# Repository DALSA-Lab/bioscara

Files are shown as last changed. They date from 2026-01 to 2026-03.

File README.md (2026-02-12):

# icon Bioscara - DALSA DIY SCARA robot arm
This repository serves to collect all information regarding DALSA's DIY robot arm **Bioscara**.
<p align="center">
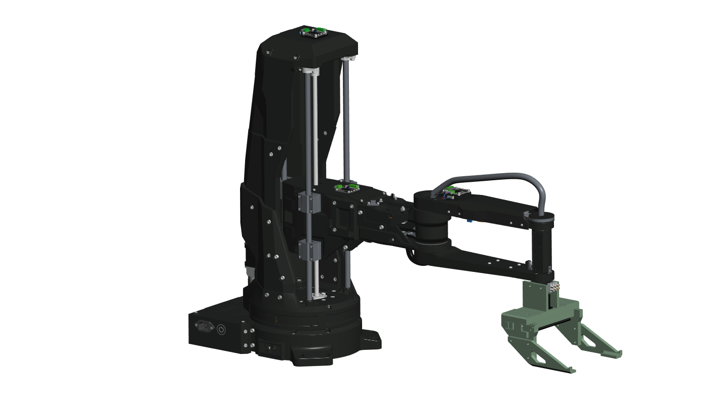
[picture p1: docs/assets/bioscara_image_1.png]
  
</p>

## Documentation and Guides
Please refer to the user guides and source code documentation at: https://dalsa-lab.github.io/bioscara/

> [!NOTE]  
> If the website is unavailable, you can find its source code in the *docs/* directory

## Repository Structure
The repository structure is based on the DALSA template.

- ***docs/***: Contains the user-guides as *.md* files and serves as the source code for the Sphinx documentation
- ***hardware/***: Contains the robots CAD model as a STEP file, STL meshes, electrical schematics and further documents
- ***installation/***: Contains installation scripts and files.
- ***lib/***: Contains the source code for the ROS2 workspace and joint firmware.
- ***test/***: Contains system test data and test protocols.

## Branches
There are three core branches which MUST NOT be deleted without appropriate replacement.
- ***main***: This branch contains the latest stable source code. Any commit to this branch will automatically trigger the build of a new documentation.
- ***bioscara_v1***: Contains the original Bioscara project by Karol Garbor.
- ***gh-pages***: contains the HTML source code hosted at https://dalsa-lab.github.io/bioscara/

## Dependencies
Currently the project has the following source-code dependencies:
- [***single_trigger_controller***](https://github.com/DALSA-Lab/ros2_control-single_trigger_controller.git) branch: *main*
- [***moveit_task_constructor***](https://github.com/moveit/moveit_task_constructor.git) branch: *ros2*
- [***moveit2***](https://github.com/DALSA-Lab/moveit2-dalsa.git) branch: *main*
- [***moveit_visual_tools***](https://github.com/moveit/moveit_visual_tools.git) branch: *ros2*
- [***pick_ik***](https://github.com/PickNikRobotics/pick_ik.git) branch: *main*

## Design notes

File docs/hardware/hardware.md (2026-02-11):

# Supplementary Assembly Instructions
The hardware has been modified in comparison the original Bioscara project.

bioscara

## Key Modifications
The key changes were:
- Replacing the MKServo42C closed-loop stepper drivers with UStepper S32 drivers
- Removing the optical endstops and replacing them with physical stop blocks for sensor less homing
- Removing the associtated wiring to the optical endstops and MKServo drivers.
- The UStepper drivers only require two signal wires (SDA/SCL) and the 24V/GND power cables.
- The electronics compartment has been simplified since the 3D-printer motherboard could be removed.
- All wires have been replaced and properly sized and terminated.
- Power distribution is achieved through terminal block mounted on DIN-rails.
- The gripper has been redesgined.

### Joint driver
The new joint driver is mounted on the back of the stepper motors just like the MKServo 42C drivers. 

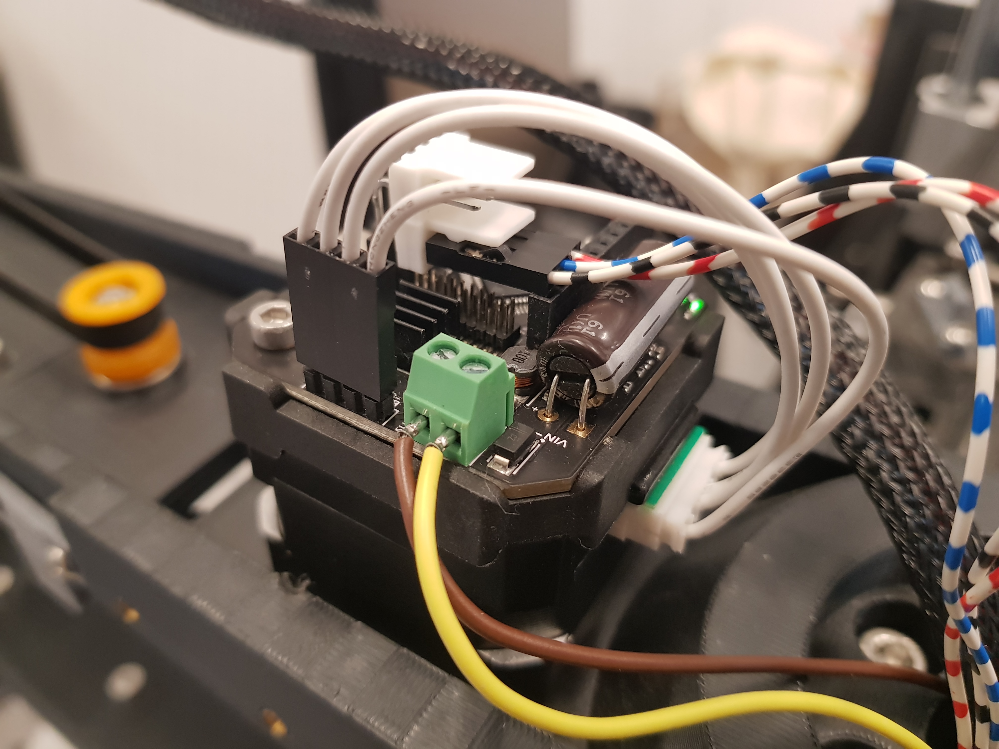
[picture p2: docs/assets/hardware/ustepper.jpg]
UStepper S32


**TO-DO:**
- Increase the cutout dimensions in the J2 covers and J1 Top cover to make room for the slightly larger UStepper mounts.

### Endstops
See the new endstops in the figures below. Their STL file can be found in the *hardware/meshes/* directory.

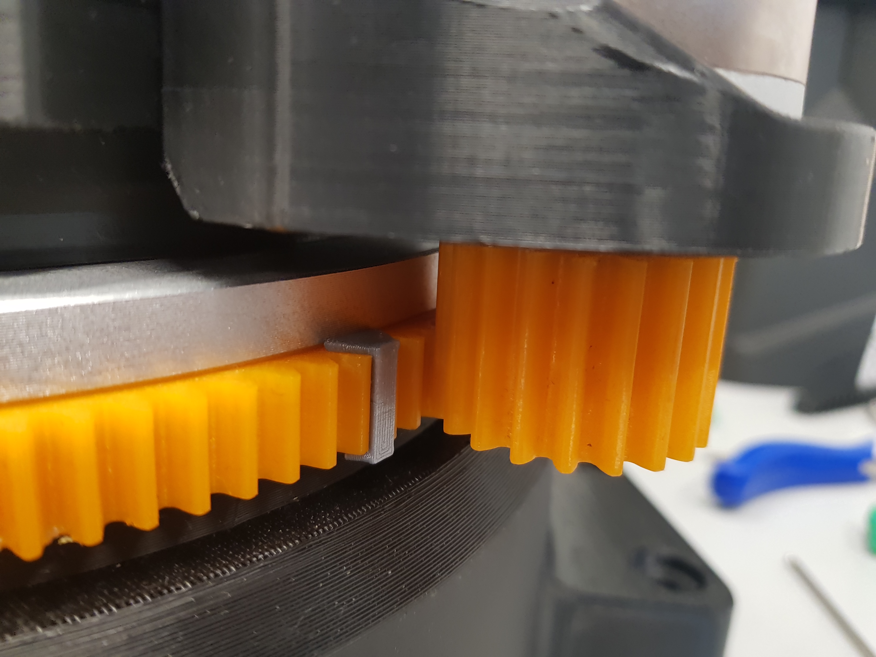
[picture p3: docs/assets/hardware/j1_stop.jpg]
J1 Endstop
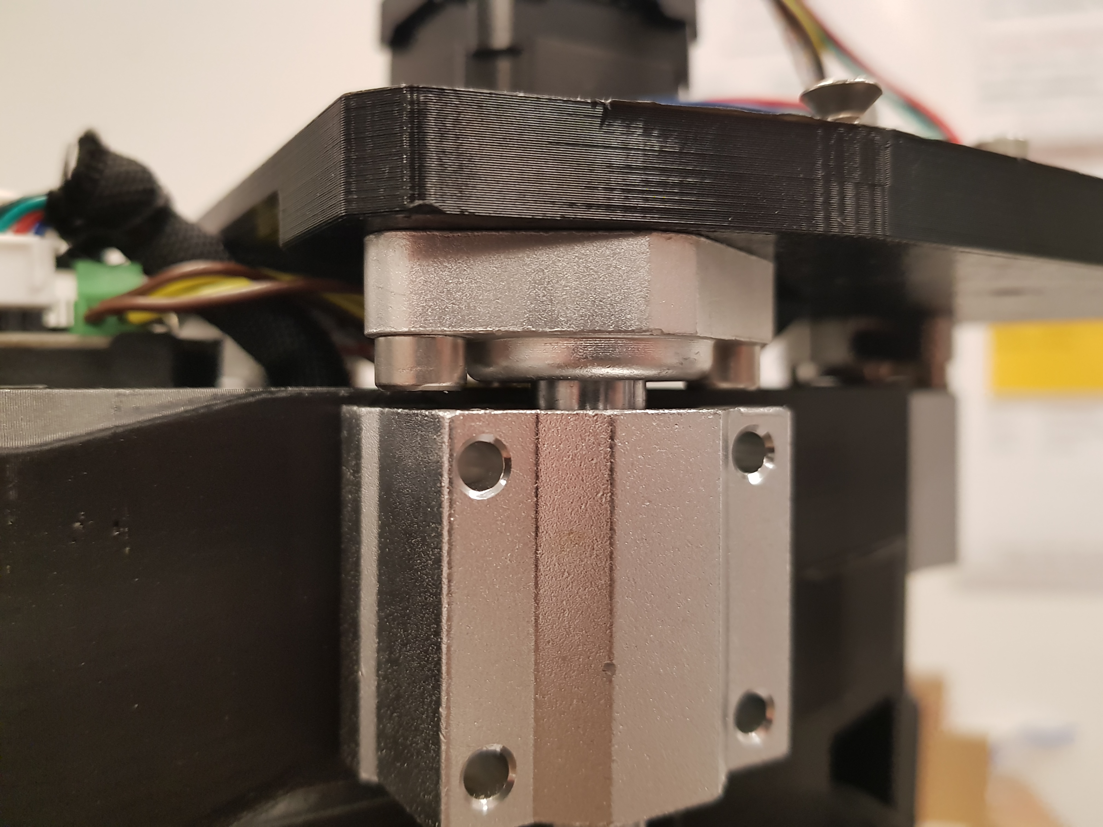
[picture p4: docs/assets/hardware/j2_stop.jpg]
J2 Endstop
|  |  |
|---|---|
| **J1 Endstop** | **J2 Endstop** |

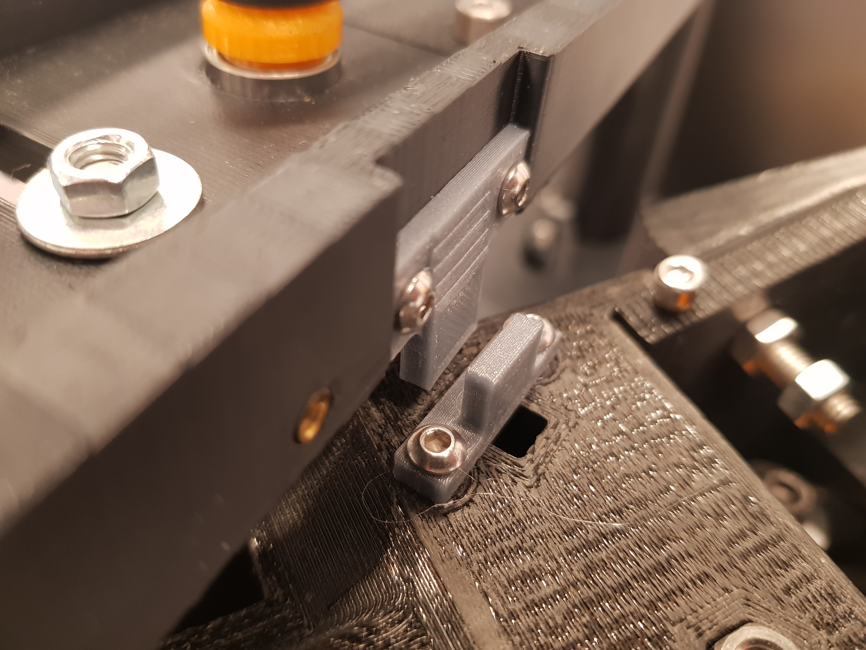
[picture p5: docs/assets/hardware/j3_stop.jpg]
J3 Endstop
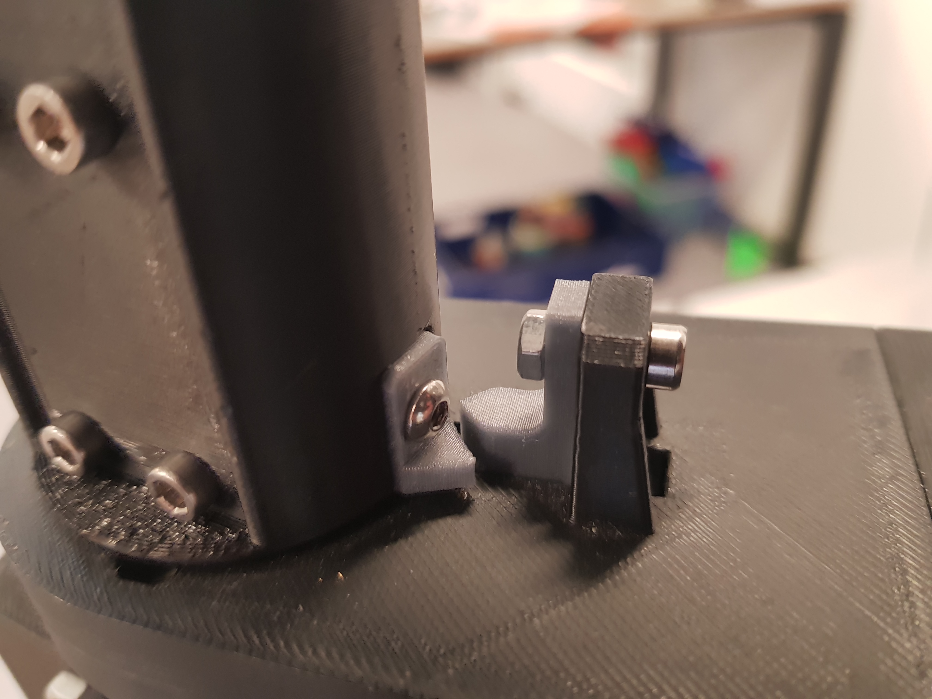
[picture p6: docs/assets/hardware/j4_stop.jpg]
J4 Endstop
|  |  |
|---|---|
| **J3 Endstop** | **J4 Endstop** |

### New Gripper Assembly
The new gripper was designed in June 2025. The results are presented in a [presentation](../../hardware/gripper_redesign_project_presentation.pdf) and [report](../../hardware/gripper_redesign_project_report.pdf).

The CAD files can be found under the *hardware/CAD Model/gripper_v2* directory.

### Tensioner Pulley Slipping
The J4 belt drive needs to be redesigned, since the tensioner pulley slips under load, releasing tension. The current workaround is the *tensioner_stop_block* that is inserted in the slot to prevent the pulley from sliding back. The stop block needs to be printed and inserted as shown in the figure. 

**TO-DO:**
- Fix the design, for example by "knurling" the surface to increase its roughness to increase friction.

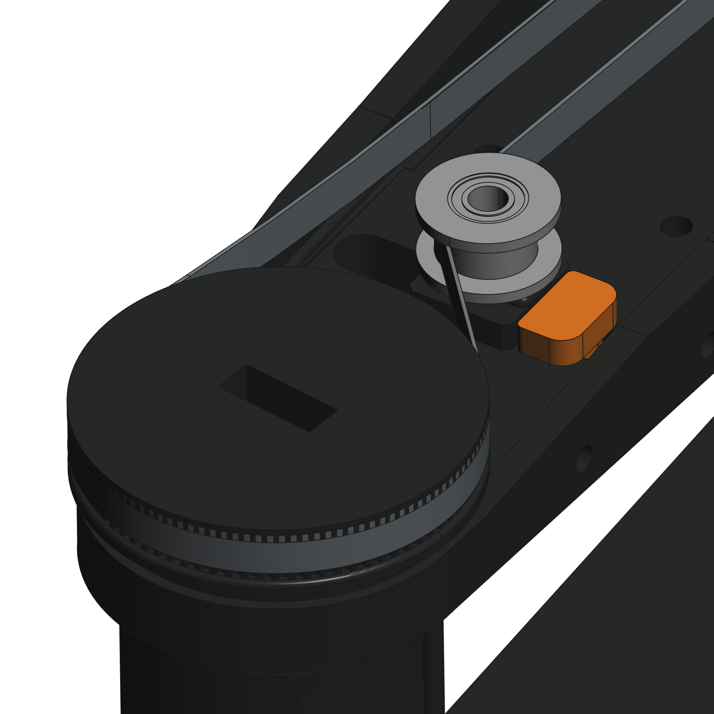
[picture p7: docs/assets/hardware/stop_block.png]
Stop Block


### Electrical Design
The electrical schematic can be found [here](../../hardware/schematics/schematic.pdf).

The schematic shows how to wire the new joint controllers and how to distribute the power in the terminal blocks.
For indicative cable lengths and wire gauges refer to the schematic as well.

:::{important}
All wires shall be appropriatly sized and terminated with spade connectors for the power supply and ferrules for screw terminals.
:::

:::{note}
Some images may display a seperate GND connection with the I2C wires. This is no longer correct. The wiring as displayed in the schematic with only a single GND wired to the power terminals is correct.
:::

The AC wiring was redone. Note that the wires are properly terminated. The power switch was replaced with a simple switch.

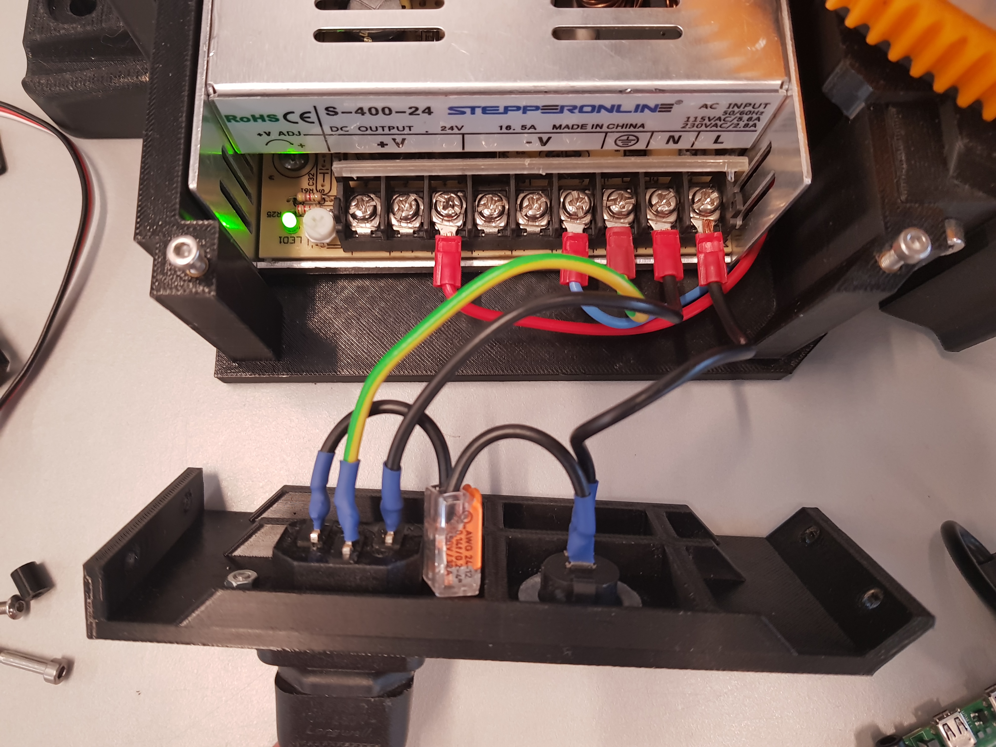
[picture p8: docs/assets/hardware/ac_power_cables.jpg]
AC cables


### Simplified Electronics Compartment
The 3D-printer motherboard and level-shifter was removed from the base plate. The number of wires was reduced. The new design is shown in the figure below. 
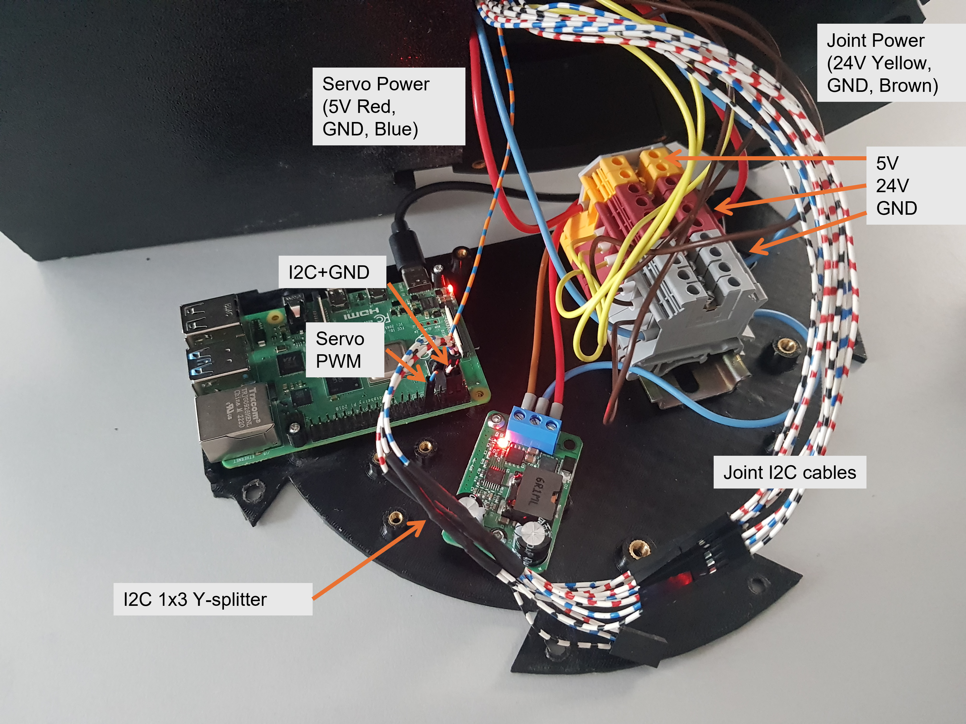
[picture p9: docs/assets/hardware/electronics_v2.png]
Electronics baseplate


**TO-DO:**
- Redesigning the electronics base plate to be able to properly mount all components. The terminal block are currently just glued in place.

## Assembly Instructions
The assmbley instructions are given in [this pdf](../../hardware/Bioscara_v2_manual_preliminary.pdf).

:::{tip}
A video of the original assembly can be found in [this  YouTube video](https://www.youtube.com/watch?v=obPP-tCtBTw).
:::

**TO-DO:**
- The instructions have only been preliminarily updated. A unified assembly guide with up to date images and information needs to be compiled.
- The current assembly guide is PowerPoint presentation. This file format is very poor for version control. The new assembly guide needs to full-fill the following criteria:
    - Platform independent: The new guide shall be easily maintainable from different platforms. PowerPoint is poorly portable between operating systems.
    - Version Control: The new guide shall be written in a text based format that supports version control such as this document or Latex.

## CAD Model and STL Meshes
The complete STEP CAD model can be found in the *hardware/CAD_model/* directory. The STEP file is compressed as a ZIP archive to be able to upload it to Github. The STL meshes for 3D-printing are in the *hardware/meshes/*.

:::{tip}
The original, now outdated, Bioscara_v1 STEP files can be found [here](https://a360.co/3SWc07A)
:::

**TO-DO:**
- The coordinate systems of the CAD model are completely wrong and need to be fixed
- The CAD model does not include the simplified arm shape used in the robot description URDF files, this remains to be added.

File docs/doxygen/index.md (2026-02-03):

# Bioscara C++ API Documentation
This is the API documentation for the Bioscara robotic control middleware based on the ROS2 framework.

Please find the key components below:
- bioscara_joint_firmware: contains the joint firmware and its associtated helper classes.
- bioscara_hardware_drivers: contains the BaseJoint, Joint and MockJoint drivers as well as the BaseGripper, Gripper and MockGripper drivers.
- bioscara_hardware_interfaces: contains the ros2_control hardware interfaces that implement the Bioscara arm and gripper hardware components in the BioscaraArmHardwareInterface and BioscaraGripperHardwareInterface respectively.
- bioscara_rviz_plugin: contains the BioscaraPanel Rviz GUI panel.
- single_trigger_controller::SingleTriggerController: contains the documentation for the SingleTriggerController.

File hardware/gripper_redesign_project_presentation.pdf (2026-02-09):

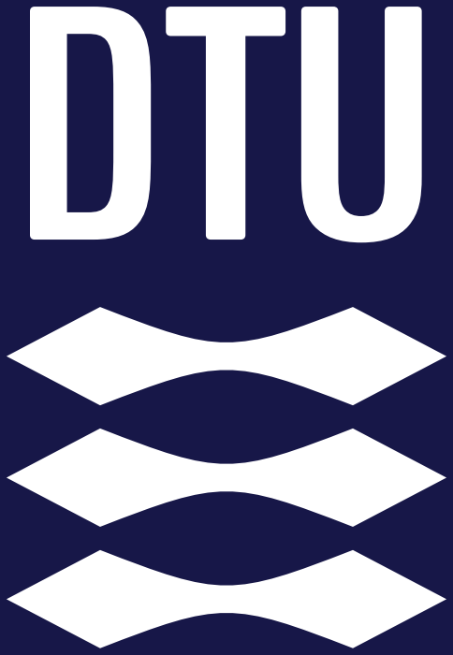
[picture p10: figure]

# Upgrading a 3D-Printed Gripper for Enhanced Robotic Handling

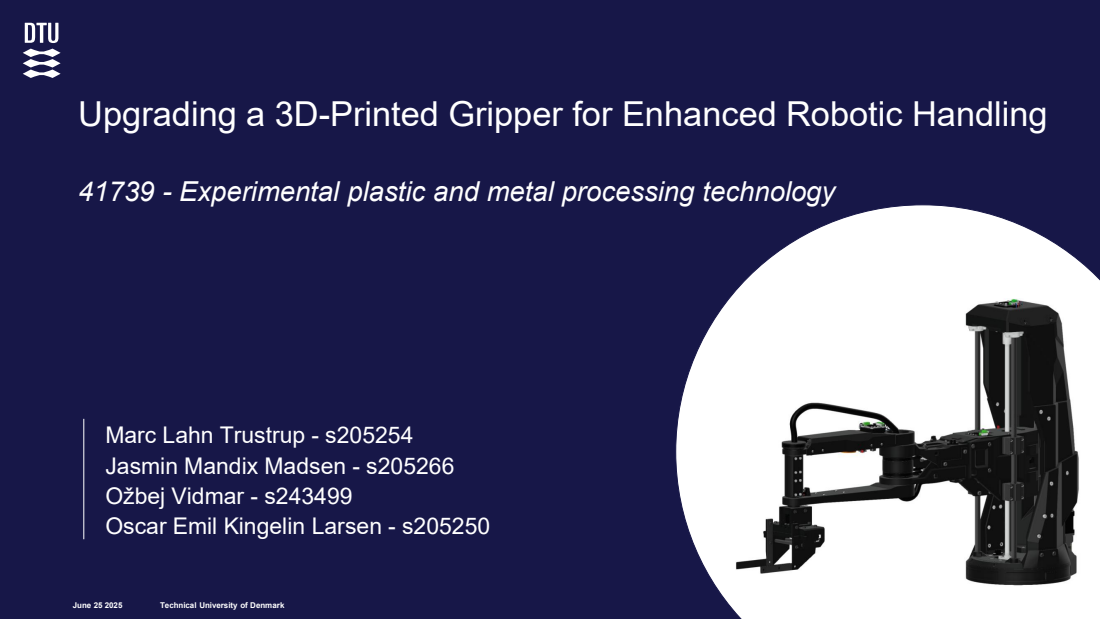
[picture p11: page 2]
June 25 2025

41739 - Experimental plastic and metal processing technology

Marc Lahn Trustrup - s205254
Jasmin Mandix Madsen - s205266
Ožbej Vidmar - s243499
Oscar Emil Kingelin Larsen - s205250

Technical University of Denmark

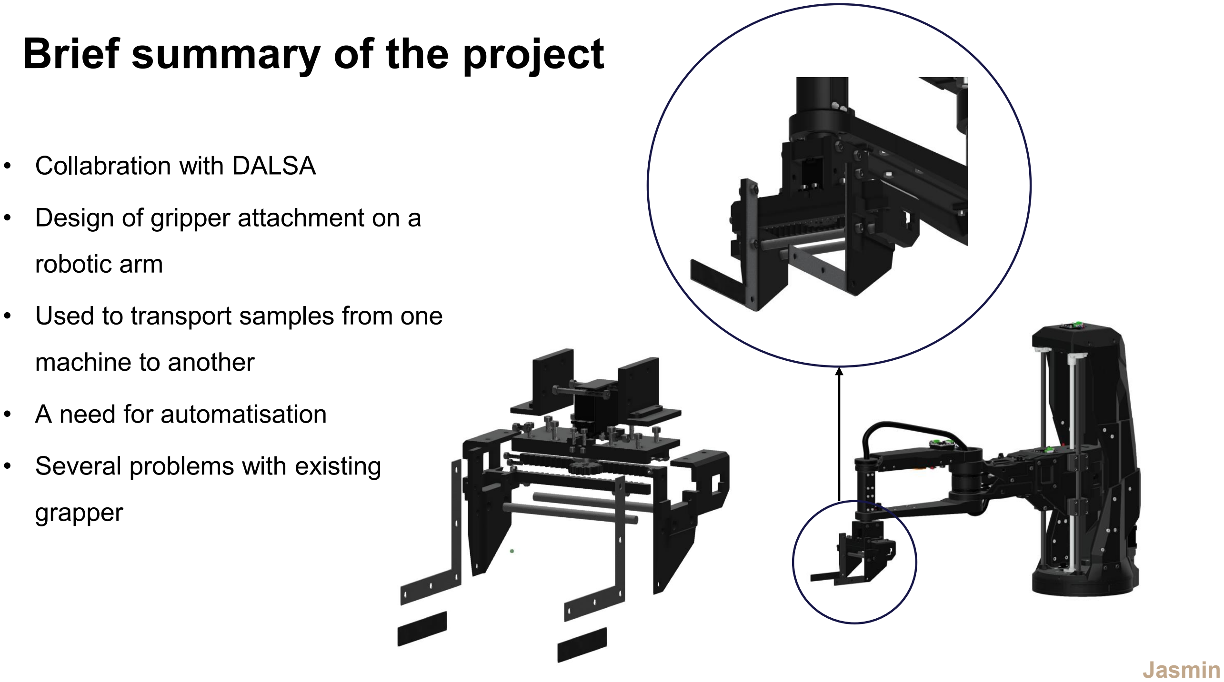
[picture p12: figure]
Brief summary of the project; • Collabration with DALSA; • Design of gripper attachment on a; robotic arm; • Used to transport samples from one; machine to another; • A need for automatisation; • Several problems with existing; grapper; Jasmin

3

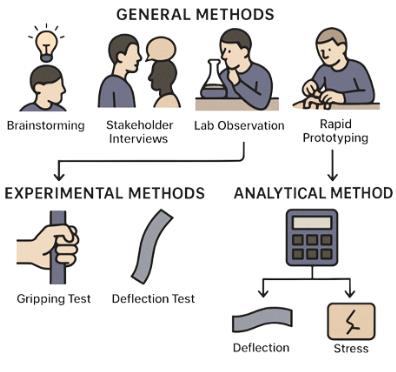
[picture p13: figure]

Technical University of Denmark | 4

# Methodology of the project

General methods
- Brainstorming
- Stakeholder interviews
- Lab observations
- Rapid prototyping

Experimental methods
- Gripping test
- Deflection test

Analytical method
- Force analysis
- Deflection
- Stress

Jasmin

# Final iteration Base

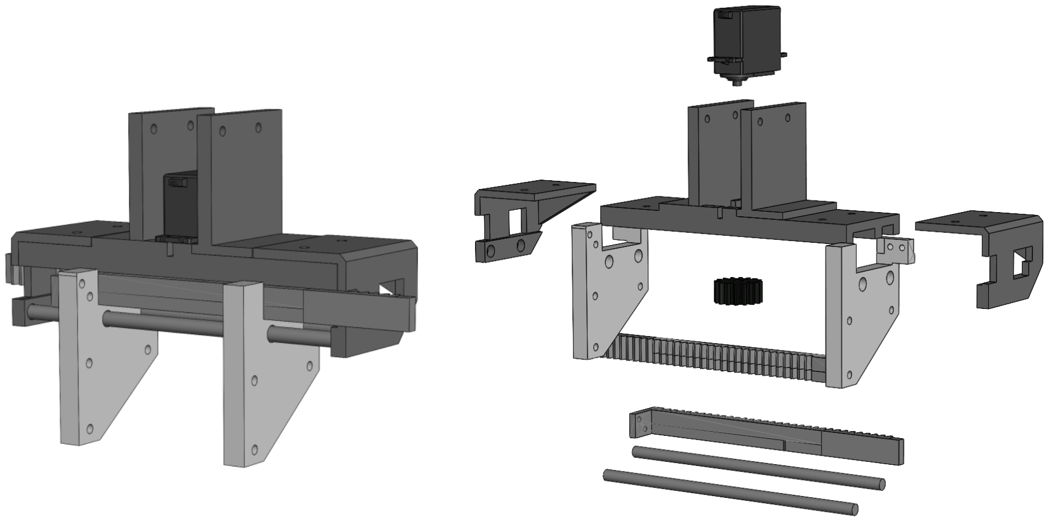
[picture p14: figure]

5

- Extended design
- Increased thickness
- Supports added
- Metal rods (new since last week)

Jasmin

# Final iteration gripper

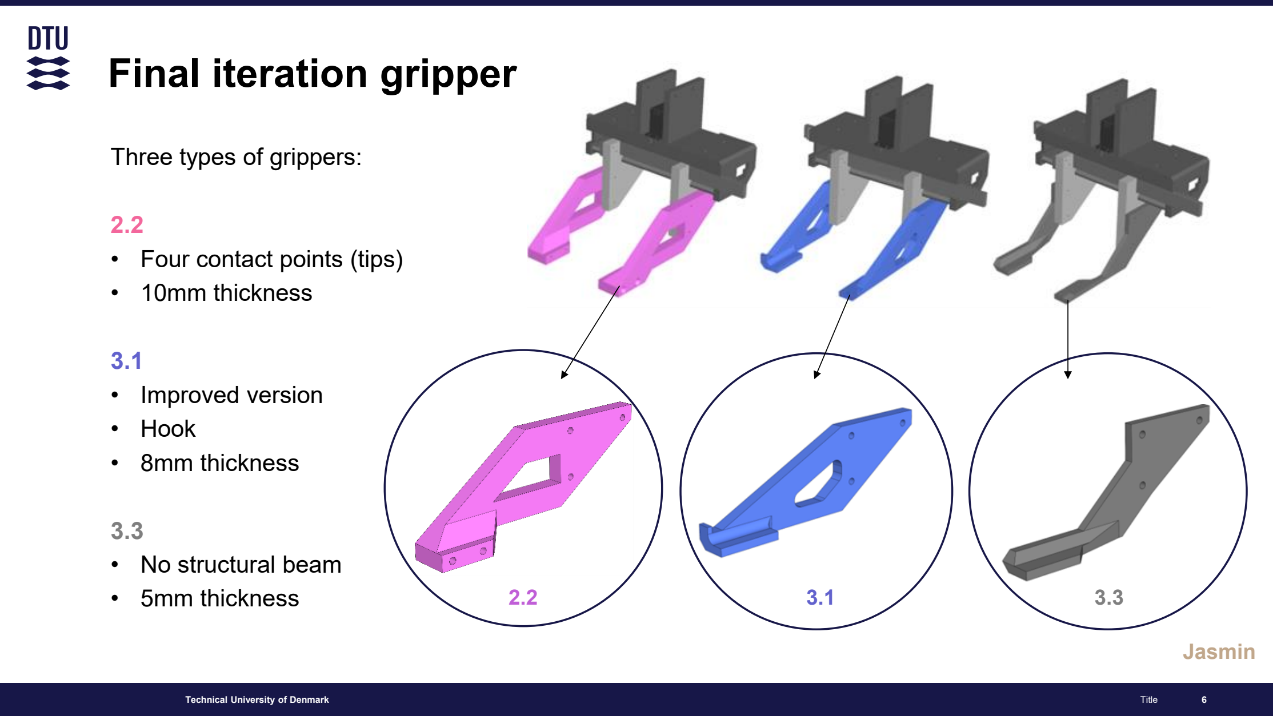
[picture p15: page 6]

Title | 6

Three types of grippers:

2.2
- Four contact points (tips)
- 10mm thickness

3.1
- Improved version
- Hook
- 8mm thickness

3.3
- No structural beam
- 5mm thickness | 2.2 | 3.1 | 3.3

Jasmin

# 1. Experiment: Gripping test

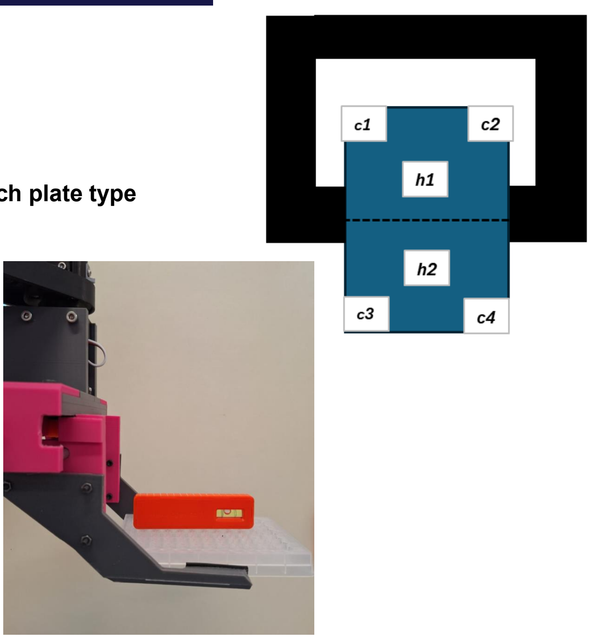
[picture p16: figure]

7

Test sequence was performed for each gripper and each plate type

1. Grip the empty plate
2. Apply the maximum load in the center
3. Apply half the maximum weight at either end
4. Apply a quarter of the total weight in each corner

Ožbej

# Results from the gripping test

8

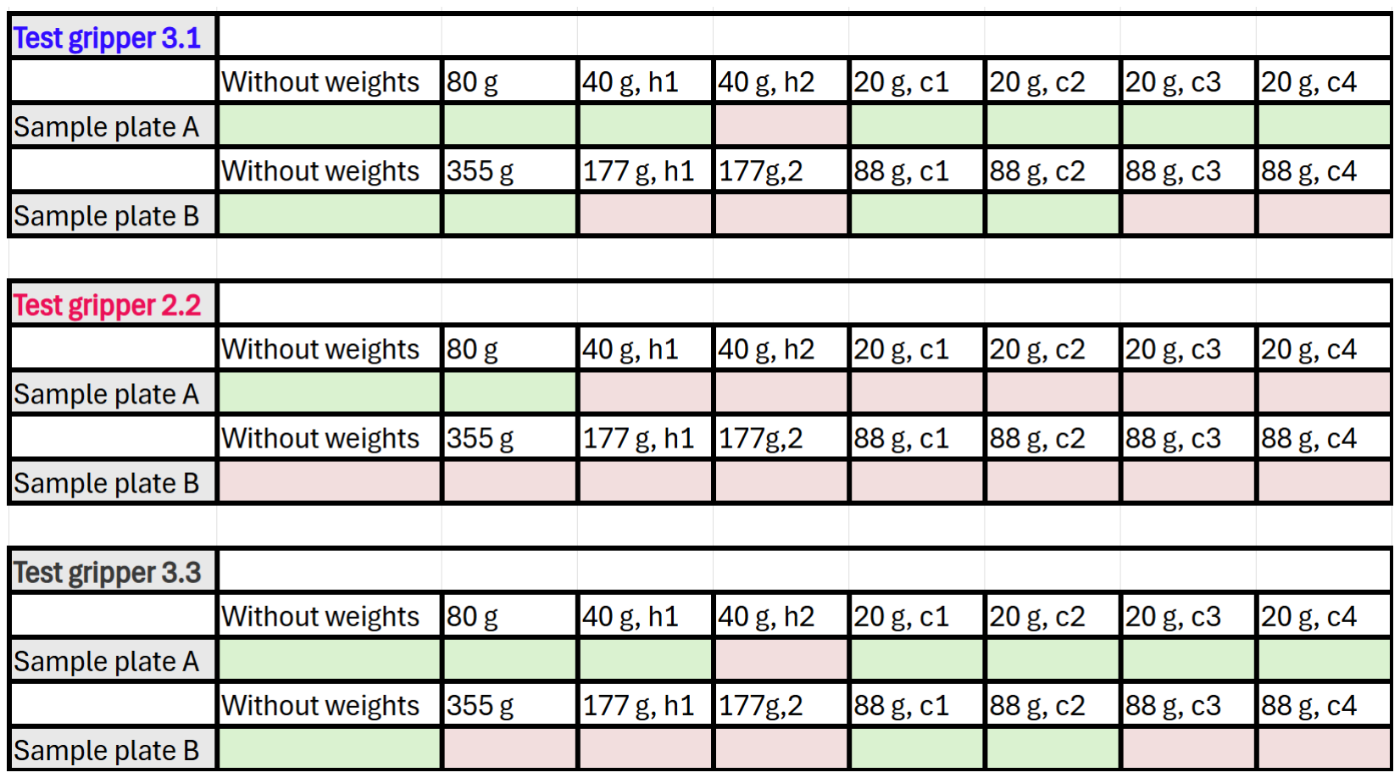
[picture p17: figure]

- Pass
- Fail

Common weakness.
- Uneven force distribution
- Cause: Likely deflection
- Pressure is applied in the back rather than in front

Succes criteria:
Able to hold for >30 seconds, 3 times

Ožbej

# 2. Experiment: Deflection test

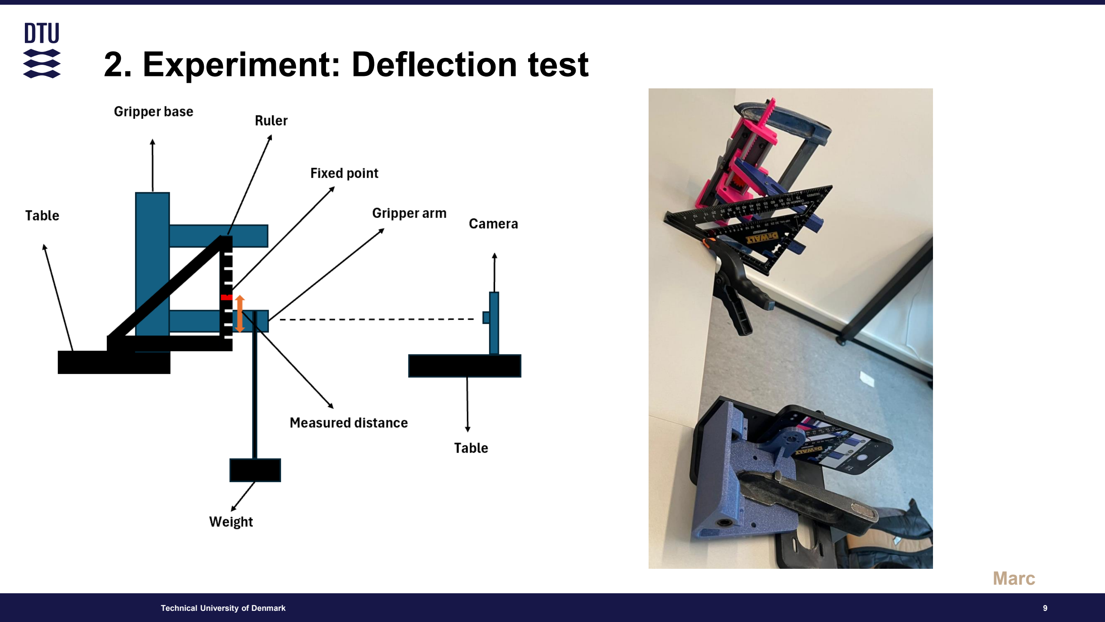
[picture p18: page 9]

9

Marc

# Results for the deflection test

10

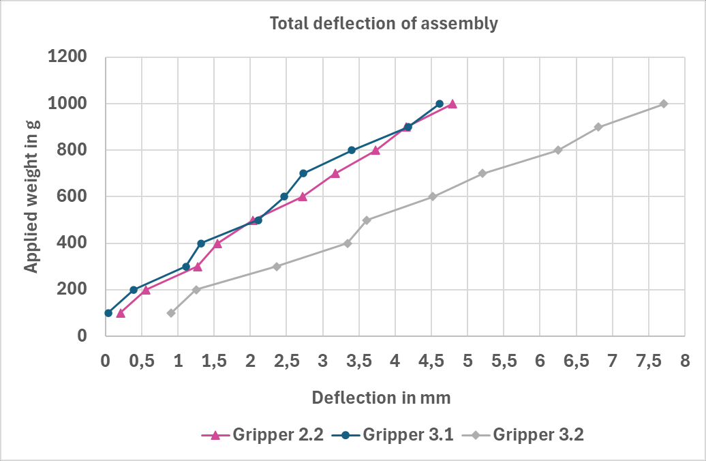
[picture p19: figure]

Gripper 3.1

- lowest amount of deflection under applied load
- maximal deflection of 4,6 mm at 1000 g.

Gripper 2.2

- The curve for the assembly with gripper 2.2 closely follows the curve of gripper 3.1,

Gripper 3.2
- Largest deflection
- maximum deflection of 7,7 mm at 1000 g.

The deflection not only occurs on the grippers but also from the whole base and assembly

Marc

# Simulations of all iterations

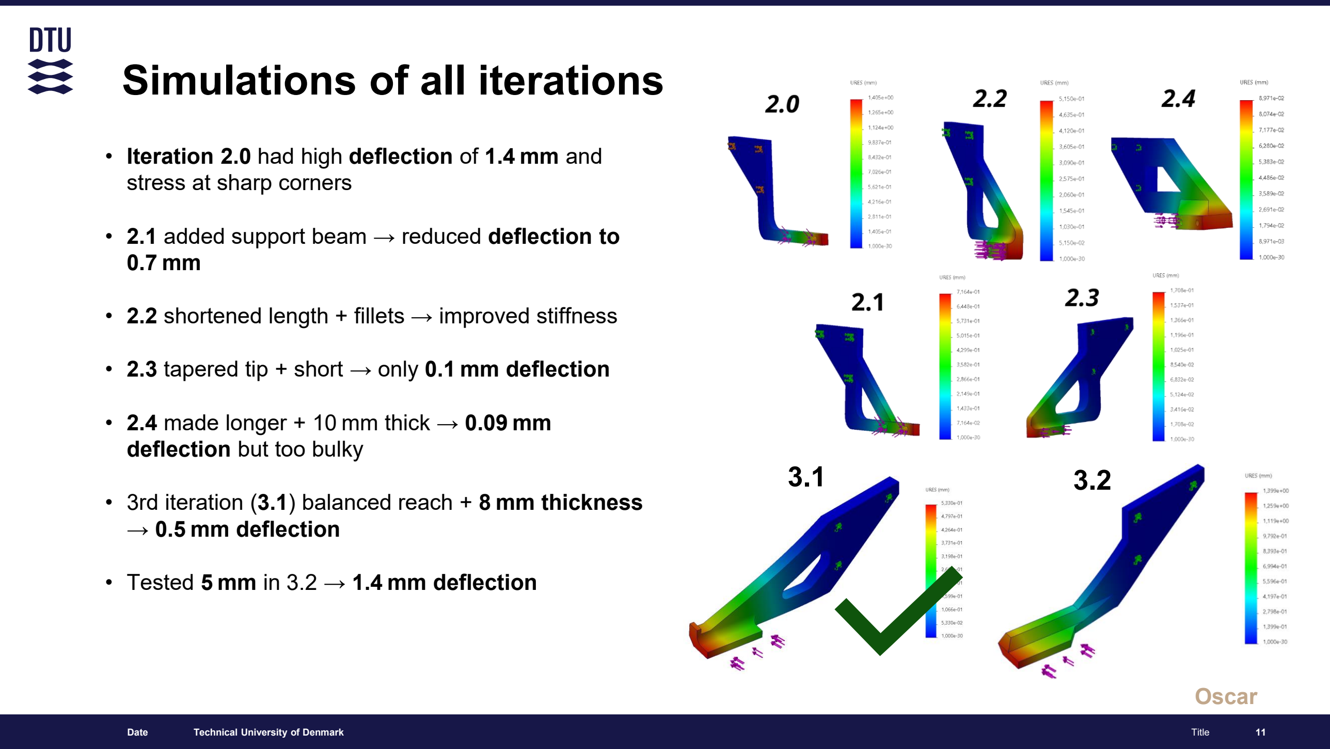
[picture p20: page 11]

Date | Technical University of Denmark | Title | 11

3.1 3.2

- Iteration 2.0 had high deflection of 1.4 mm and stress at sharp corners
- 2.1 added support beam → reduced deflection to

### 0.7 mm

- 2.2 shortened length + fillets → improved stiffness
- 2.3 tapered tip + short → only 0.1 mm deflection
- 2.4 made longer + 10 mm thick → 0.09 mm deflection but too bulky
- 3rd iteration (3.1) balanced reach + 8 mm thickness → 0.5 mm deflection
- Tested 5 mm in 3.2 → 1.4 mm deflection

Oscar

# Comparison of experimental and simulation data

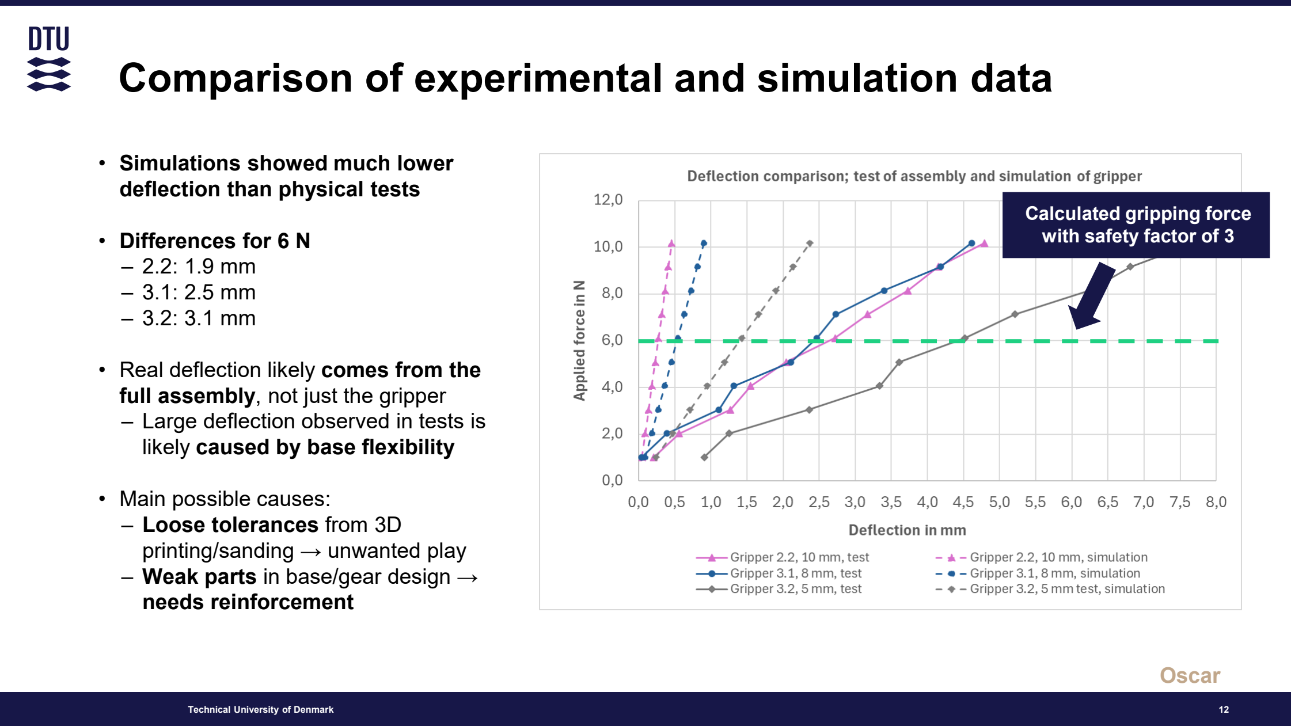
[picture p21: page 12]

Technical University of Denmark | 12
- 2N force was applied to each gripper (Safety factor of 2)
- Calculated force needed to hold plate filled with water
- Simulations showed much lower deflection than physical tests
- Differences for 6 N
– 2.2: 1.9 mm
– 3.1: 2.5 mm
– 3.2: 3.1 mm
- Real deflection likely comes from the full assembly, not just the gripper
– Large deflection observed in tests is likely caused by base flexibility
- Main possible causes:
– Loose tolerances from 3D printing/sanding → unwanted play – Weak parts in base/gear design → needs reinforcement

Calculated gripping force
with safety factor of 3

Oscar

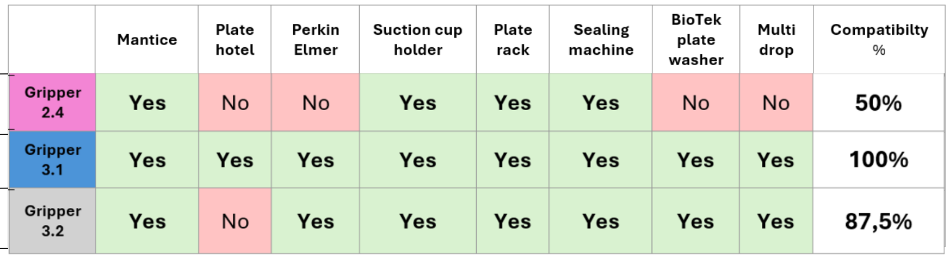
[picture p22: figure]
Calculated gripping force with safety factor of 3

Technical University of Denmark | 13

# Machine compatibility

- 2N force was applied to each gripper (Safety factor of 2)
- Calculated force needed to hold plate filled with water

### Gripper 3.1 is the best choice – Still problems with deflection – Tolerances for the robot arm is lower than 1 mm is needed

Test
deflection
(6N) in mm

Simulation
deflection
(6N) in mm
0,27 | 2,72
0,54 | 2,47
1,43 | 4,52

Oscar

# Proposals for future work

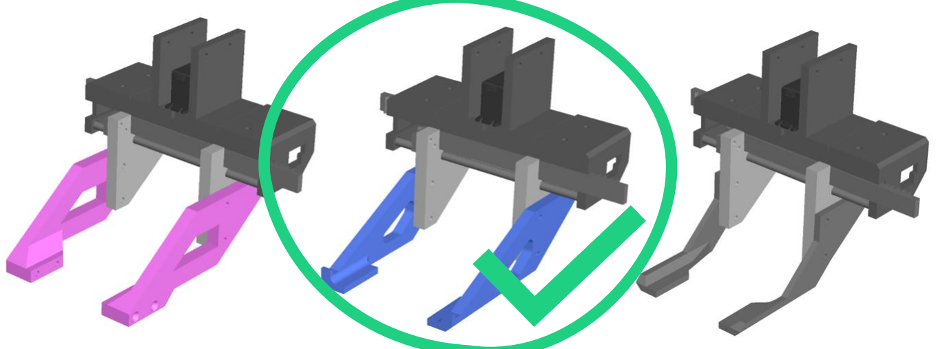
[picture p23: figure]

14

- Gripper 3.1 can be used if:
- Redesign of base and gears is strengend (make it

more stable and do simulation)

- Can be improved with other materials to lower weight

and make parts thinner with less displacments

- Introduce metal components (Al to keep low weigth,

thinner and less displacment)

- Look into 3D printable material with carbon fibers

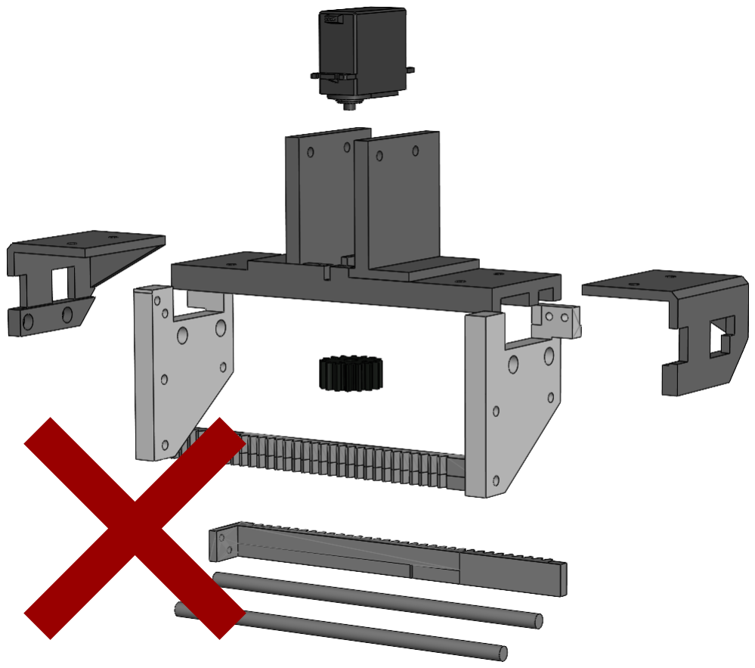
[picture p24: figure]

Oscar

# Thanks for listening ☺

15

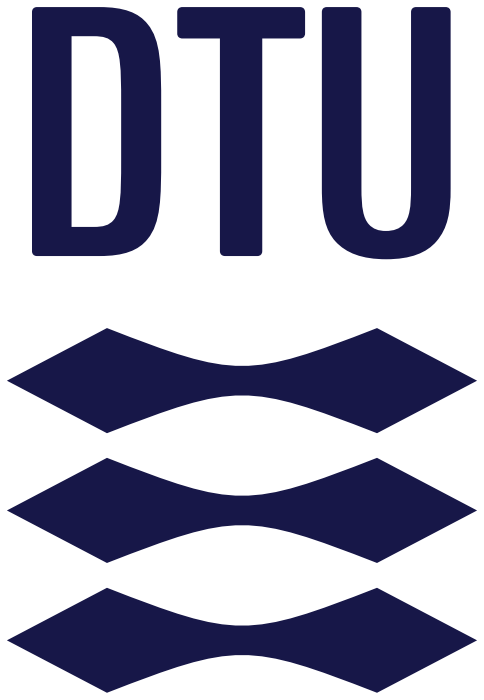
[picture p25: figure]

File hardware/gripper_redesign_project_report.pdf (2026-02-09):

Group 2 | 41739 | 26. juni 2025
0 | P a g e

# UPGRADING A 3D-PRINTED GRIPPER FOR ENHANCED ROBOTIC HANDLIN

### 41739 - EXPERIMENTAL PLASTIC AND METAL PROCESSING TECHNOLOGY

MARC LAHN TRUSTRUP - S205254 JASMIN MANDIX MADSEN - S205266 OŽBEJ VIDMAR - S243499
OSCAR EMIL KINGELIN LARSEN - S205250

## JUNE 2025

## Contents

Introduction | 2
Problem formulation | 3
Product Design Requirements | 5
Material selection | 9
Brainstorm | 11
First iteration prototype | 14
Grippers | 14
Base | 15
Limitations and improvements (after 1 iteration) | 16
2
nd iteration | 17
Final iteration | 20
Final iteration gripper: | 21
Machine capabilities | 22
Experimental plan with an overview in table form | 23
Description of experimental procedure | 24
Results | 26
Description of theoretical/numerical analysis (Force analysis) | 29
For sample plate A | 30
For sample plate B | 30
Payload Limitation and Practical Gripping Capacity | 31
Force analysis results | 31
2nd Iterations | 32
Final Iterations | 34
Comparing with previous gripper | 35
Comparison with experimental results | 36
Lifetime | 37
Evaluation of metric | 39
Proposals for future work | 39
Appendix | 44

## Introduction

Dalsa describes itself as a space for interdisciplinary projects to explore and develop new technologies within the life science industry, with a vision to be a leading facility in the development and implementation of future automation technology in life-science, R&D, and manufacturing (Dalsa frontpage, u.d.)
The field of bioengineering is crucial, but despite the availability of advanced, fully automated solutions, they remain largely accessible only to large commercial organizations that can afford significant investments. For academic institutions, the high cost of purchasing, implementing, and maintaining automated equipment limits accessibility, forcing reliance on manual labor. This not only reduces efficiency but also introduces issues like human errors or fatigue. (Gabor, 2024)
To address these challenges, a previous master's thesis project, “Advancing Laboratory Automation in Life Sciences through Robotic Design and Implementation” by Karol Gabor, focused on developing a cost-effective robot arm. This project aimed to automate lab procedures by developing an accessible system that relies on automation rather than manual labor. Specifically, the project proposed a robotic arm designed to automate the process of transporting sample plates from and to lab machines. The goal was to create a modular and cost-effective arm that could be easily adapted and duplicated for different environments and equipment, by making the whole project open-source and utilizing 3D printing.
An essential component of this robot system is its end-effector, or gripper system, which is responsible for picking up and holding sample plates, While the previous project successfully developed a 3D printed robot capable of transporting plates, the gripper design has some limitations- It lacks the stiffness and grip precision required to reliably hold specific target samples.
Therefore, the task of this project is to redesign and fabricate an improved gripper for enhanced robotic handling. This involves analyzing the limitations of the current design, developing a new 3D printed gripper with enhanced stiffness and holding capability, and validating its performance through testing on the robotic arm.

## Problem formulation

An analysis of the existing gripper, developed in the previous project, identified several key limitations and problems:
Not 3D printable: The original gripper was identified as being made of a metal sheet. One of the project's goals was to create a fully 3D printable robotic arm for ease of replication and modularity. The goal for the new gripper is therefore to be 3D printed. Stiffness: A critical issue of the original gripper is the lack of sufficient stiffness and grip precision. Instead of securely grasping sample plates with adequate force, the existing claws would bend and “give”. This might also be a problem in 3D printed structures, as plastics typically exhibit lower stiffness compared to materials like metal, necessitating careful design optimization to achieve the required rigidity.
Extending: The current design only grasps samples from a single direction. A specific user requirement for the improved design was the ability to grab samples from multiple directions, accommodating the diverse loading and unloading mechanisms of various laboratory machines.
One-way gripping: The original gripper could only grab samples from a single direction. A specific user requirement for the improved design was the ability to grab samples from multiple directions, accommodating the diverse loading and unloading mechanisms of various laboratory machines.
Loading on 3D printed Gears: The existing setup places a large force on the 3D printed gears and gear rack, which means the rack bends. While 3D printing offers benefits for rapid prototyping and cost reduction, the printed gears have inherent limitations regarding loading-bearing capacity and functional reliability.


Figure 1: Identified problem with the existing gripper system.

Figure 2: Existing gripper handling sample plate

Based on the identified problem and requirements for the gripper system, the following problem formulation has been formulated:
This 3-week project focuses on redesigning and fabricating an improved gripper for an existing robotic arm developed in a previous student project. The current gripper lacks the stiffness and grip precision required to reliably hold a specific target sample. The goal is to analyze the limitations of the current design, develop a new 3D-printable gripper with enhanced stiffness and holding capability, and validate its performance through testing on the robotic platform.

## Product Design Requirements

To redesign the gripper system, a set of requirements was formulated based on the identified problems with the existing gripper as well as additional wishes from users in the DALSA lab.
The sample plates:
The following picture is an example of a sample plate. All plates are the same length and depth, but usually different heights.

Key product design requirements for the new gripper system:
Plate dimensions: The gripper must be designed to handle sample plates in dimensions 8,5 cm x 12,5 cm, but varying heights. This means that the gripping mechanism must accommodate different plate heights and weights while maintaining a secure hold.

Sample plate

Figure 3: Example of sample plate.

Gripper Scenarios/ Interaction Methods: The gripper must support diverse methods of plate handling, which have been identified in the DALSA lab.
From the top: For many machines, the gripper needs to grab and place plates from the top. This requires the robot arm to be positioned above the plate, with the gripper engaging the plate from its sides.
From the sides: For certain machines and especially for the plate hotels, the gripper must be able to grasp the plate from the side while the robot arm is positioned horizontally. This enables the robot to position the plate from the side and place it into the hotel.
From the bottom: When retrieving plates from sample hotels, the gripper needs to pull the samples out, likely from the bottom, and then grab the sides of the plate.
Suction cups: The design must also account for the fact that some machines handle plates from the top using suction cups. This implies the gripper design should not obstruct the top surface of the plate, or it should be able to interact with plates that have been handled this way.


Figure 4: The different grip scenarios

Needs/metrics Matrix
Based on the problems identified with the existing gripper as well as the different gripper scenarios, a needs/metric matrix was made. The needs identified are:
- The solution should fit the existing robot without too much redesign.
- The solution should be able to handle all sample sizes and grab from both the short and long sides.
- The geometry of the solution should be 3d printable
- The material chosen should allow for 3D printing
- The gripper should not plastically deform when force is applied.
- The gripper should be stiff enough as to “give” or elastically deform when force is applied
- It should grab the sample firmly without slipping, requiring a sufficient friction coefficient
- The solution should allow for easy replacement - design for disassembly
- The solution should be able to accommodate several gripper scenarios / different machines
- The solution should be cheap
- The material should be able to withstand lab conditions and cleaning
- The product lifetime should be at least 3 years
- These needs were then used to create a needs/metrics matrix, where each need was matched with a corresponding metric, creating a way to measure the success of each need.


Table 1: Needs, Metrics Matrix

Specifications
Based on the metric, each need was given a unit, a minimum value, as well as a target value. Based on these specifications, the redesigned gripper system can be effectively measured through direct comparison as well as functional testing. Each metric provides a quantifiable target of characteristics that allow for clear evaluation.

Table 2: Specification table

## Material selection

For material selection, the program “Ansys Granta Edupack” was used to plot a performance index for the selected materials. As one of the project's requirements is a fully 3D printable solution, only plastics with the ability to be processed by 3D printing were considered.
A plot with Price on the y-axis and Volume per unit of stiffness on the x-axis was created. This index was chosen because the gripper solution needs to be as thin and stiff as possible while keeping the price as low as possible, to ensure that the solution can be replicated easily.

Figure 5: Material analysis in Granta Edupack.

PLA (Polylactic acid)
PLA is a biodegradable thermoplastic made from renewable resources. It is one of the most popular materials for 3D printing. It has a tensile strength of 50 to 70 MPa. PLA is easy to print, gives a good surface finish, and is low-priced. The main disadvantages of PLA are low heat resistance and poor chemical resistance.
PETG (Polyethylene Terephthalate Glycol)
PETG is a modified form of PET (used in plastic bottles), enhanced with glycol to prevent crystallization and make it more printable. The result is a tough, impact-resistant, and slightly flexible material that combines the properties of PLA and ABS. It has a tensile strength between 50 and 60 MPa, and it has good chemical resistance.
ABS (Acrylonitrile butadiene styrene)
ABS is a petroleum-based thermoplastic polymer known for its high strength, impact resistance, and durability. Its tensile strength ranges between 40 and 50 MPa, and it is easy to 3D print. The primary disadvantage of ABS is that it contracts when cooled, resulting in layer separation and warping.
PEK (Polyetherketone)
PEK is a semicrystalline high-performance thermoplastic known for exceptional mechanical strength, chemical and thermal resistance, and dimensional stability. Its tensile strength ranges from 100 to 120 MPa. PEK is 3D printable but requires industrial-grade equipment due to its extreme processing demand.
The graph indicates that the optimal material for a thin and stiff gripper is PEK with 20-30% carbon fiber. With this material, high stiffness can be achieved, allowing the design to be as thin as possible. However, it is also costly, and an industrial grade 3d printer would be needed. This would be a good option for further investigation, however, not for the current scope of this project.
Another option would be ABS with the addition of carbon fiber. ABS is an easy material to print, but without carbon fiber, it will not give sufficient stiffness. PETG is a suitable material due to its good chemical resistance; however, it is more challenging to print. The graph also reveals that PETG has lower stiffness than PLA.
PLA was chosen as the most suitable material for the 3D printers available for this specific project. PLA is easy to print, low in price, commonly used, and gives good stiffness. The orientation of 0° was used for 3D printing PLA, as it exhibits the highest tensile strength in this orientation. (Syaefudin, 2023)

## Brainstorm

Based on the needs, brainstorming was conducted. Several ideas were found and evaluated.
The Ideas:
Snap fit solution:
The first idea explored using snap fits to attach different grippers to the robot arm. The gripper should therefore be interchangeable, allowing for customization. However, this idea focused most on the attachment of the gripper and the geometry of the gripper itself. This idea scores second-to-last as the complexity of the solution was too high, as attaching the gear as a snap fit would need very fine accuracy.

All in one solution


For this solution, several types of grippers are attached to the arm. Changing the gripper would, therefore, not be necessary. However, this would require lots of gears, and the arm would need to move more in the x,y, and z directions. This would also require a lot of additional coding for the arm to operate. Because of this, this solution scored the lowest on complexity, being too complex for the scope of the project.

Figure 6: Idea 1


Figure 7: Idea 2

Universal base with snap-fit
The Idea behind this sketch is that the base of the gripper would be universal. The base has snap-fit holes. On the universal base, you could put different types of fingers to hold the plate. That is good, because then you can easily and quickly change gripper fingers. The problem here would be that 3d printed snap-fits are not stiff enough for the stability of the gripper.

Attached with bolts
This idea presents a universal base for the gripper. With bolts and nuts, you can tighten different gripper fingers. The bots and nuts will make better connections than snap-fit. With that, you can have different gripper claws for different applications, and you can easily change them. We would apply rubber at the edge of the gripper’s fingers for better grip and increased friction between the plates and fingers. This idea standardizes the gripper’s base.

Gripper integrated into the claw mount:
This idea shows us the gripper claw in one piece with the base of the gripper. This will give the gripper more sturdiness. The downside is that when you have to change the grippers for another type of claw, you have to disassemble the whole gripper.

Figure 8: Idea 3

Figure 9: Idea 4


Figure 10: Idea 5

360
This gripper would be redesigned. It would be able to turn 360°. It would be able to pick the plates from the top and the side. And it would give us stability and accuracy, which is essential for robots.
The downside of this gripper is that it is quite complex. We would need to change the motor and 3D print complex parts.

Rating:

When evaluating the ideas, a scoring system was utilized, assigning a score from 1-5 in four key categories. These categories were crucial for determining the feasibility and effectiveness of proposed solutions for the robotic arm.
The four main criteria were:
- Easy replacement: Is the solution easy to add to the robot? Would it be easy to replace or interchange parts?
- Complexity: Are there several parts to be manufactured? Is geometry complex? The simpler, the easier!
- Cost: Would the solution be costly? Or cheap to manufacture?
- Universal positioning: Would the solution accommodate the requirement for several gripping scenarios?

Table 3: Scoring table for assessing different gripper ideas
No. | Idea | Easy Replacement (1 is bad, 5 is good) | Complexity (parts, Geometry) (1 is bad, 5 is good) | Cost (1 is bad, 5 is good) | Universal positioning (1 is bad, 5 is good) | TOTAL
1 Snap-fit | solution | 4 | 2 | 3 | 5 | 14
2 All in one | solution | 4 | 1 | 2 | 5 | 12
3 Universal base | with snap-fit | 4 | 4 | 3 | 5 | 16
4 Attached with | bolts | 4 | 4 | 5 | 5 | 18

Figure 11: Idea 6

5 Gripper | integrated into the claw mount | 4 | 5 | 4 | 5 | 18
6 | 360 | 4 | 1 | 4 | 3 | 12

## First iteration prototype

Following our idea generation phase, we began developing and testing physical prototypes to evaluate mechanical performance and compatibility. This section presents the first iteration of our gripper and base design, focusing on material choice, structural challenges, and initial functionality.
Grippers
Based on idea five from the brainstorming (see Table 3) and based upon research made on existing types of grippers., the first gripper was designed with inspiration from the original gripper mounted on the robot arm. The idea behind this approach was to evaluate how the same mechanical concept would perform when produced by 3D printing plastic instead of metal. To ensure compatibility with the existing base system, the Gipper was mounted directly onto the rods, integrating it into the claw mount. The thickness of the gripper was set to 10mm. This value was chosen based on the dimensions of the original 3d printed components and served as a starting point for evaluating stiffness. The idea was to test the mechanical performance of the 10mm profile under loads and adjust the thickness accordingly in future iterations, based on the observed stiffness and deflection.


Figure 12: 1st. iteration gripper mounted on the | Figure 13: CAD file of the 1st. iteration gripper

original base system.
The first iteration of the 3D printed gripper faced several challenges, including issues with stiffness and its physical dimension, which could be a problem in laboratory settings. To account for the lack of thickness in the plastic material, the gripper was made very thick to ensure no bending when picking up the sample plate. However, this made it almost too bulky and could potentially cause problems in the laboratory environment, where space and fit are important.
It was suggested that we try designing a gripper with four points of contact instead of two, as this would improve stability when picking up a sample plate with uneven weight distribution.
Base
To address the extension-related issues identified, a new, longer base was printed. It was also decided to add a universal base to make the change of grippers quicker and easier without having to disassemble the entire base. This idea was based on suggestion no. 4 from the brainstorming session (see Table 3). Implementing the universal base would require an iteration and redesign of the gripper mount to ensure a proper fit.

Figure 14: The first iteration of the base with the extended system
While creating an extended base seemed like a straightforward solution, it introduced several new problems that affected both the precision and mechanical performance of the gripper.
Warpage:
Warpage was observed in several locations, likely caused by the printer settings or the increased length of the printed parts. This was particularly problematic for components like the rack gear, where stability is critical to ensure proper function. A possible solution for future iterations would be ribs to reduce deformation.
Printed rods vs. metal rods:
The original included metal rods. However, to simplify the first iteration, these were replaced with 3D printed rods. Due to the limited precision of FDM printing, the rods required extensive post-treatment to ensure a smooth and round surface. And even after the surface treatment of the rods, the plastic rods were not smooth enough and lacked sufficient stiffness.
Insufficient stiffness:
The new base lacked stiffness. With the larger and longer design, rigidity was compromised, as the thickness of the base was not increased to match the extended dimensions. This became a problem during use, as an unstable base can lead to imprecise, unsafe, or unreliable handling. Improving the structural integrity of the base would therefore the essential in future iterations.

## Limitations and improvements (after 1 iteration)

Based on the results of the first iteration prototype as well as the issues identified in” Product Design Requirements”, it was decided to divide the original requirements along with the new insights into two categories: Need to have and Nice to have. This distinction served as a guide for the next iteration by clearly prioritizing core functionality over secondary features.

Need to Have | Nice to have
- A new, stiffer base able to extend the
full length of the sample plate
- Easy to add and change grippers
- Defines maximum dimensions to ensure the gripper fits within the “hotel.”
- Moderate stiffness to prevent bending when transporting samples
- Able to grab sample plates from multiple angles
- Able to fully extend to hold the sample plate
- Fully 3d printable design
- Improved gear mechanism to ensure proper closing

- Contact the sample plate at four points for improved transport stability

2

## nd iteration

Based on the first iteration as well as requirements, a 2nd iteration base and grippers were designed and printed.
2

nd iteration base:
For the second iteration, it was decided – due to limited programming skills and time constraints – to continue using he original motor and core mechanical setup. The focus was instead placed on improving the gripper mechanism itself. However, to allow the gripper to properly extend and grab the sample plate from both the long and short sides, several modifications to the base design were necessary.
The first iteration prototype lacked sufficient stiffness; both the spur and the gear racks were somewhat unstable. To address this, the following changes were implemented.
- Extended and reinforced several structural parts
- Increased gear thickness to improve mechanical stability
- Introduced a support beam and a one-part design for added rigidity
- Added angle supports along the sides
- Integrated mounting hole to attach different grippers and cutouts for the thickened gears


Figure 15: 2and iteration - Gears and base.
Despite the changes, testing revealed that the base still had a significant amount of “give” when force was applied. The flexibility of the plastic used meant that even with stiffer grippers, the overall structure could still deform. This highlighted the need for an even more stable base in the final iteration.

2

nd iteration grippers:
The second iteration of the grippers focuses on structural improvements to address the deflection and instability issues observed in the first design. A key modification was the addition of a support beam to enhance rigidity and the load-bearing performance (see Error! Reference source not found. for all designs made in the 2

nd iteration).
Two gripper designs were tested:
Gripper 2.3: Shorter and slimmer design
- More compact and easier to fit within tight spaces
- Less stiff compared to the longer version, but lighter.
Gripper 2.4: Longer and stiffer design
- Increased length and additional support
- Required a thicker profile to maintain stiffness

Test and comparison of the two grippers:


The two grippers were tested in the lab, to find if they would successfully fit in the different machines and be able to place a sample plate in different machines. For most machines, the gripper both succeeded in securely gripping the plates, but two main areas of problem as found, which will be explained below.
Machine 1:

Figure 16: The two 2nd iteration grippers, 2.3 and 2.4

Figure 17: Different grippers in use cases.
For the first machine, gripper 2.3 fit and functioned well, with sufficient clearance on both sides, to securely grab the sample plate. In contrast, gripper 2.4 was too thick at the tip, and did not have enough clearance to securely grasp the plate from the machine. It would require at least 10-15mm of clearance to operate properly.

Machine 4 – Sample plate hotel:


Figure 18: Different grippers in use cases.

For the hotel, the performance of the grippers also varied. It was observed that gripper 2.3 had tips that did not protrude enough to ensure proper placement. Additionally, the support beam interfered with the insertion process, preventing the gripper from pushing the plate fully into the hotel. Gripper 2.4 was longer, which allowed it to successfully place the plate into the hotel without alignment issues.
In a different version of the sample hotel, both grippers encountered difficulty extracting the plate from its slot. This revealed a general limitation in the design:
- Neither gripper could effectively pull the plate out horizontally from the enclosed holder
- A proposed solution is to incorporate small hooks or extensions at the top of the grippers, allowing the robot to pull the plate toward itself before gripping the sides.
Both 2

nd iteration grippers had strengths and weaknesses in different machine contexts. Gripper 2.3 provided greater stability and grip strength, but its size limited compatibility. Gripper 2.4 offered better maneuverability but lacked sufficient reach in some situations. As a result, a final iteration was developed, aiming to combine the advantages of both designs. Based on this, as well as the force analysis (see Error! Reference source not found.), a final iteration was made.

## Final iteration

Based on the previous iterations and learnings, a final iteration of both the base and the grippers was developed for the project. The goal of this version was to use the final iterations for experimental testing as well as to compare and contrast.
Final iteration base

For the final iteration of the base, the 2nd iteration was used, but metal rods were attached instead of the 3d printed ones. This was an attempt to make the whole base sturdier, as well as making the opening and closing mechanism smoother.
Final iteration gripper:
Below are the three final iterations presented. These will be further analyzed and investigated through physical tests and simulations.
Gripper 2.4
This gripper is previously described in the above section. The gripper has 4 contact points when it grabs a sample plate; therefore, this was interesting to test. The thickness of the base of the gripper is 10 mm, making this the thickest gripper and the one that uses the most material, with a weight of 47 g.

Figure 19: Gripper 2.4.
Gripper 3.1
Gripper 3.1 is an improved version of gripper 2.1, with longer reach and improved stiffness due to improved geometry. Further, a hook at the tip of the gripper was added for the purpose of being able to pull out plates, e.g., a sample plate hotel, where space on the side and at the top is limited. The thickness of the base of the gripper is reduced compared to 2.2, with a thickness of 8 mm and a weight of 34 g.

Figure20: Gripper 3.1.

Gripper 3.2
Gripper 3.2 was an attempt to make a design using less material, by minimizing the thickness and removing the structural beam as in 3.1. The thickness of the base of the gripper is 5 mm, and it has a weight of 21g.

Figure 21: Gripper 3.2.

## Machine capabilities

As part of our evaluation metric, we assessed the compatibility of each gripper design with various lab machines (see appendix 4). Our target was to achieve at least 60% compatibility, with higher compatibility considered even more desirable.
We tested gripper versions 2.3 through 3.2 in the lab and summarized the results in the table below:

Table 4: Compatibility of grippers with different lab machines and plates.

| Mantice | Plate hotel | Perkin Elmer | Suction cup holder | Plate rack | Sealing machine | BioTek plate washer | Multi drop | Compatibilty %
Gripper 2.3 | Yes | No | Yes | Yes | No | Yes | Yes | Yes | 75%
Gripper 2.4 | Yes | No | No | Yes | Yes | Yes | No | No | 50%
Gripper 3.1 | Yes | Yes | Yes | Yes | Yes | Yes | Yes | Yes | 100%
Gripper 3.2 | Yes | No | Yes | Yes | Yes | Yes | Yes | Yes | 87,5%

Gripper 3.1 achieved the highest compatibility score at 100%. This was primarily due to the addition of a hook feature, which enabled it to pull plates out of the plate hotel. However, it’s important to note that compatibility with the plate hotel assumes a specific programmed motion for placing and retrieving plates (see Figure XX).


Figure 22: Motion for placing and taking plates from plate hotels with gripper 3.1 iteration
Gripper 2.4 encountered significant issues due to its thickness, which caused it to collide with the sides of some machines. Gripper 2.3 performed reasonably well but had limitations: its short arms couldn’t reach into the plate hotel effectively, and it lacked a central grip point on the plates for maximum stability.
Gripper 3.2 showed promising compatibility but lacked the hook feature required for plate hotel interaction (also shown in Figure XX). Additionally, it exhibited displacement issues under force, which will be discussed in a later chapter.

## Experimental plan with an overview in table form

To evaluate the performance and stability (stiffness) of the different gripper designs, an experimental plan was developed. Three grippers were tested to determine which design would provide the most reliable grip under various loading conditions.

Figure 23: Three chosen iterations of grippers (2.2, 3.1, 3.2) for further investigation and test.
Sample plates
Two different sample plates were used to represent the standard lab conditions. Plate A: 96-well, round bottom assay, height 1,5 mm, well volume: 500μL. (Round bottom assay plate, 2025)
2.4 | 3.1 | 3.2

Plate B: 24-well, deep well plate, height: 4,5 mm, well volume: 10mL. (Deep well plate, 2025)


Figure 24: Sample plates used for test.

Test overview

Test Scenario | Succes-criteria
Hold plate without load | Able to hold for >30 seconds, 3 times
Hold plate with full load (weight applied to center) | Able to hold for >30 seconds, 3 times
Hold plate with ½ load applied end | Able to hold for >30 seconds, 3 time
Hold plate with ¼ load in each corner | Able to hold for >30 seconds, 3 times
Deflection test (weight applied at tip of each gripper) | Minimal deflection, no permanent deformation
Machine compatibility test | Above 70%
Force analysis | Maximum deflection of 1mm
Figure 25: Overview of experimental setup

## Description of experimental procedure

Gripping test
Due to limitations with the robot's programming, the gripping tests were carried out manually. Each gripper design was mounted into the same base, which in turn was attached to the robotic arm. Manual force was used to close the gripper around the sample plate. Although the motor was not powered during testing, the passive clamping force generated was sufficient to securely hold the plates under test conditions.
The following test sequence was performed for each gripper and each plate type (A and B)
1. Grip the empty plate to assess fit and grip
2. Apply the maximum load (equivalent to a
water-filled plate) in the center
3. Apply half the maximum weight at either end of the plate to simulate uneven loading (h1 and h2)
4. Apply a quarter of the total weight in each corner (to simulate uneven leads) (c1, c2, c3, and c4)

Deflection test


A test was performed to measure the deflection of the entire gripper system (base and grippers). The test system is illustrated in figure xx.

Figure 27: Deflection test setup of the entire gripper system.

Figure 26: Illustration of where weight was distributed on the sample plate

The gripper system was clamped to a table, to make sure it was securely attached. A ruler was placed behind the system. On the ruler, a fixed point was set for later image analysis. A phone was securely placed in front to take a picture of the system (see picture of test setup, appendix 1). Weight was applied to one gripper; a picture was taken, and the deflection could be measured in the image analysis software Fiji (ImageJ).
The following test sequence was performed for each gripper:
1. A control picture before the weight is applied.
2. Pictures with different weights are applied, 100 g, 200 g, …, 1000 g.
3. Image analysis in software Fiji (ImageJ).
a. The control picture taken at step 1 is used to set the scale and to measure the control distance from the fixed point on the ruler to the bottom of the gripper arm.
b. The scale is then set on the pictures of the system, where different weights are applied, and the distance from the fixed point and the bottom of the gripper is measured.
c. The measured distance is then subtracted by the control distance to find the total deflection at a given point.
In this test case, the experiment was not repeated. It is, however, recommended to repeat the test to estimate the margin of error.

## Results

In the following section, the results from the two experimental tests and the three grippers are compared in their performance.
Gripping test
Gripper 3.1:
This gripper demonstrated the overall best performance.
- With sample plate A, it passed all tests, except when a load was applied to the front half of the plate (h2)
- With sample plate B, it failed to hold the plate when weight was applied to either end (h1 and h2) or in the front corners (c3 and c4)
These results suggest that while the blue gripper provided the best grip effect, it lacked sufficient force transmission towards the front.


Figure 28: Grip test results for gripper 3.1 (pass/fail)
Gripper 2.4
This design used four screws as contact points, but it consistently underperformed, likely due to the “give” of the base which caused the grippers to deflect too much, making only 2 of the 4 contacts points grabbing the sample plate.
- The gripper only succeeded in holding sample plate A with no load and an evenly distributed maximum load.
- In all other tests, especially with uneven or heavier loads, the gripper failed to maintain a secure hold.
- The gripper scratched the sample plates and could potentially poke a hole if the force applied was sufficient.
This shows that a point-based gripping system without surface contact may not be reliable for varying plate types and weight loads.

Figure 29: Grip test results for gripper 2.2 (pass/fail)
Gripper 3.2
The grey showed a similar performance profile to the blue gripper, but a slightly reduced capacity.
- It was capable of securely holding sample plate B without any load, and when weight was applied to the backend corners (c1 and c2)
- However, when the same weight was applied to the front corners, the plate would tilt.
- When larger loads were applied, it would also fail to maintain a firm grip.

Figure 30: Grip test results for gripper 3.2 (pass/fail)

Test gripper 2.4
| Without weights | 80 g | 40 g, h1 | 40 g, h2 | 20 g, c1 | 20 g, c2 | 20 g, c3 | 20 g, c4
Sample plate A
| Without weights | 355 g | 177 g, h1 | 177g,2 | 88 g, c1 | 88 g, c2 | 88 g, c3 | 88 g, c4
Sample plate B

Test gripper 3.3
| Without weights | 80 g | 40 g, h1 | 40 g, h2 | 20 g, c1 | 20 g, c2 | 20 g, c3 | 20 g, c4
Sample plate A
| Without weights | 355 g | 177 g, h1 | 177g,2 | 88 g, c1 | 88 g, c2 | 88 g, c3 | 88 g, c4
Sample plate B

A shared weakness
All three grippers demonstrated a common weakness. The front half of the plate (h2) was consistently the most unstable area under testing for both sample plates (A and B). This is likely due to the force distribution as well as the deflection of the whole gripper system. Because the gripping force originates high up, near the mounting point between the base and the gripper, there is a loss of force transmission towards the tip of the gripper. Combined with the flexibility of the base, this results in a non-uniform force distribution, with significantly more pressure applied at the rear contact points than at the front. This mismatch is especially problematic under asymmetric load conditions, where the plate's weight is not evenly distributed.
Deflection test
Figure 12 presents the total deflection of the complete assembly under varying applied weights for three different grippers. The x-axis represents the deflection ranging from 0 to 8 mm, while the y-axis shows the applied weight ranging from 0 to 1200 g. The complete dataset can be found in appendix 2.


Figure 31: Result from a test of the total deflection of the assembly with the 3 different grippers.
In general, across all test cases, there is a trend suggesting a linear relationship between the applied weight and deflection.
Gripper 3.1

For the assembly with gripper 3.1 we see the lowest amount of deflection under applied load with a maximal deflection of 4,6 mm at 1000 g.
Gripper 2.4
The curve for the assembly with gripper 2.4 closely follows the curve of gripper 1, but with an average deflection of 0,2 mm higher under the applied loads.
Gripper 3.2
The assembly with gripper 3.2 is where the most deflection occurs. With a deflection of approximately 1 mm with an applied weight of 100 g and a maximum deflection of 7,7 mm at 1000 g.
The test in general shows that there is substantial deflection under applied loads and that the deflection not only occurs on the grippers but from the whole base and assembly. In the next section the actual deflection that comes from the grippers will be investigated.

## Description of theoretical/numerical analysis (Force analysis)

During our design iterations, multiple force analyses were conducted to determine the optimal geometry of the plastic gripper. This was important to ensure that the gripper remained stiff with minimal deflection when gripping a plate, while also being thin enough to fit into various machines such as those used in hotels.
To define the applied force in our SolidWorks simulations at the gripper’s contact points, a calculation was needed to estimate how much force is required to lift a sample plate. The friction coefficient of rubber on impact-resistant polystyrene was used as a reference, as it is the closest material found to PLA. For soft rubber, which was used in the contact areas of the gripper, the friction coefficient ranges from 1.6 to
1.87. (See Figure 32)

Figure 32: Friction coefficient of soft rubber with respect to the plastics: 1) polytetrafluoroethylene, 2) rigid polyvinyl chloride, 3) polyethylene P4020-C, K, 4) polyethylene P2010-T, 5) polymethylmethacrylate, 6) impact-resistant polystyrene. (D.S.)
We selected the lower friction coefficient value of 1.6 for our calculations to ensure a conservative estimate for safety and reliability. To estimate the gripping force required from each side of the gripper, we used the following formulas:

F =

m · g
μ

and Feacℎ gripper =

F
2
For sample plate A
For sample plate A, the filled weight is 80 grams, which corresponds to 0.080 kilograms. The gravitational force acting on the plate is:

0,080 kg ∗ 9,8

m
s

2 = 0,7840 N

Using a friction coefficient of 1.6, the required total normal force is:

0,7840 N
1.6

= 0,49 N

Dividing the force between the two grippers:

0,49 N
2

= 0,245 N
For sample plate B
For sample plate B, the filled weight is 355 grams, or 0.355 kilograms. The gravitational force is:

0,3550 kg · 9,8

m
s

2 = 3,479 N

The required total normal force is:

F =

3,479 N
1,6

= 2,174 N

Dividing between both grippers:²,174 N
2

= 1,087 N

This analysis shows that to lift a filled sample plate A, each gripper must apply a normal force of approximately 0,25 N, while for the heavier sample plate B, each gripper must apply approximately 1,08 N. These values were used to define the boundary conditions in the SolidWorks simulations.
Payload Limitation and Practical Gripping Capacity
According to the referenced master’s thesis, the robot system was able to handle a total payload of 750 grams with the old gripper arm already attached. The old gripper assembly, including its base, had a combined weight of 330 grams. The new and improved base with two grippers attached weighs 407 grams.
This means the available payload in the new setup is calculated as:

750 g + 330 g − 407 g = 673 g
Under the new design, the gripper must therefore be able to safely lift and hold items weighing up to 673 grams. Based on our earlier friction analysis, this is entirely achievable with the updated configuration. To verify this, we calculated the required gripping force using the following steps:

0,673 kg · 9,8

m
s

2 = 6,595 N

F =

6,595 N
1,6

= 4,122 N

4,122 N
2

= 2,061 N

To ensure reliability and accommodate potential variation in surface conditions, manufacturing tolerances, or material fatigue, we applied a safety factor in our SolidWorks simulations. With a safety factor of approximately 3, this results in a required maximum design force of around 6 N per gripper.

## Force analysis results

In this chapter, we present the simulations conducted during the development of our gripper design, specifically for all Iteration 2 models and the final Iteration 3 model. These simulations were essential in guiding the evolution of the gripper geometry and ensuring that the final design met the mechanical and dimensional requirements for use in various medical machines designed for handling plastic sample plates.
The project began with Iteration 1, where we created a simple physical prototype based on our initial concept and idea generation process. This version was 3D printed without any simulation or numerical analysis. The purpose was to quickly explore form, scale, and physical interaction with the sample plates. While this gave us valuable hands-on feedback, it lacked the mechanical validation needed for further development.
2nd Iterations
During the second iteration, we began integrating simulation into our design process. At this stage, we focused purely on structural performance without applying any safety factor. Each simulation was run with a 2 N force applied to a single gripper arm to analyse how different geometries performed under realistic gripping conditions.
Below are the results from the simulations:


Figure 33: Stress simulations of all second iterations in SolidWorks, with a 6 N force applied at the contact points of a single gripper.


Figure 34: Displacement simulations of all second iterations in SolidWorks, with a 6 N force applied at the contact points of a single gripper 35
From the results of the displacement and stress simulations, we observed clear differences between each sub-version of the second iteration (see Figure 33 and Error! Reference source not found. 23). The initial version, Iteration 2.0, experienced very high deformation, with a maximum displacement of approximately 1.4 mm. Such a level of flex would likely compromise the gripper's ability to hold and place medical plates. Additionally, high stress concentrations were found at sharp internal corners, indicating potential failure points under repeated loading.
In response, Iteration 2.1 introduced a supporting beam to improve stiffness. This modification reduced the displacement to around 0.7 mm, effectively halving the previous result. However, stress concentrations at the corners remained a concern. For Iteration 2.2, we made two key design changes: the length of the gripper was shortened to reduce tip flexibility, and fillets were added to all critical corners to minimize sharp stress transitions. This led to a more stable design with improved deformation.
Building on this, Iteration 2.3 implemented a tapered profile by maintaining a thicker base while gradually thinning toward the gripping tips. This adjustment significantly improved performance, bringing the maximum displacement down from 0.5 mm to just 0.1 mm. This improvement was likely due to both the reduced mass at the ends and more efficient load distribution. The fillets from Iteration 2.2 were retained to continue relieving stress in critical areas.
While Iteration 2.3 was functionally successful, it was still limited in reach and needed better compatibility with the plate-machines in the lab. Therefore, Iteration 2.4 focused on combining high stiffness with extended reach by increasing the overall thickness to 10 mm and elongating the arm. This change further reduced the displacement to 0.09 mm, meeting the structural performance targets while allowing access to plate storage systems such as the medical hotels.
However, during physical testing in the lab, we discovered that the increased thickness created new issues. The gripper was now too thick to fit into several machines and could no longer grip plates from both the long and short sides. These limitations highlighted the need for further refinement in Iteration 3, with a focus on balancing stiffness, reach, and geometric compatibility.
It is also worth noting that in all second iteration simulations, the maximum von Mises stress observed was approximately 2.4 · 10⁶ N
m²

, which is significantly below the yield strength of the PLA-like material used, set at 5.69 · 10⁷ N
m²

,. This confirms that,
structurally, none of the designs approached the material’s failure limit under the simulated load of 6 N, and all geometries stayed well within the elastic range of the material.
Final Iterations
The third iteration was developed to solve the issues identified in iteration 2.4, specifically the need to reduce thickness to fit into lab machines while ensuring the gripper remained long enough to reach into the plate hotels. For these simulations, a safety factor of 3 was introduced to ensure the design could handle extreme loading conditions without permanent deformation.

Figure 36: Stress simulation of Iteration 3.1 in SolidWorks, with a 6 N force applied at the contact points of a single gripper.


Figure 37: Displacement simulation of Iteration 3.1 in SolidWorks, with a 6 N force applied at the contact points of a single gripper.

Figure 38: Stress simulation of Iteration 3.2 in SolidWorks, with a 6 N force applied at the contact points of a single gripper.


Figure 39: Displacement simulation of Iteration 3.2 in SolidWorks, with a 6 N force applied at the contact points of a single gripper.
For Iteration 3.1, we designed a version capable of handling all expected scenarios. The arm was extended in length, and a supporting beam was added for stiffness and placed so it would not interfere with plate hotel placement. Based on earlier tests, we also added a small hook at the tip to help pull out plates without depending entirely on gripper thickness.
Further testing in the lab revealed that we could grip plates near their end, insert them halfway into the hotel, and then use a programmed motion to push them in completely (see figure XX). With this insight, we retained an 8 mm thickness and achieved a maximum deformation of 0.5 mm (see figure XX), with no significant stress concentration (see figure XX). In contrast, iteration 2.4 was too thick at 10 mm and had a 30 mm wide tip, making it incompatible with both the hotels and other placement systems. Iteration 3.1 reduced the tip width to 20 mm and the thickness to 8 mm, solving both problems.
To explore the limits of thinness, we developed one final version: Iteration 3.2. The goal was to test if a 5 mm thick gripper without a support beam could still function. Although we saw no immediate need for the beam during our lab observations, we were concerned it might interfere with machine edges in future use cases. We added various tapered features to reinforce the geometry.
Simulation results for Iteration 3.2 showed a relatively high deformation of 1.4 mm (see figure XX), about three times more than 3.1. However, no stress values exceeded the yield strength of the material (see figure XX), confirming that the design remained structurally sound.
Comparing with previous gripper Finally, compared to the gripper that was on the machine when we started the project, we assumed that the original gripper was made of galvanized steel with a thickness of 1.5 mm. By measuring the force applied at different levels, we found that at 20

Newtons, the old, galvanized steel gripper exceeded its yield strength and began to deform plastically (see figure XX).
When performing the same test on our Gripper 3.1, which has a thickness of 8 mm, we found that it did not exceed its yield limit. Additionally, the displacement was only 1 mm, compared to 4 mm for the metal gripper. This clearly shows that our plastic gripper outperforms the old one in terms of both stiffness and yield strength.
However, it is important to note that our design is significantly thicker than the original metal gripper, which is a trade-off in terms of material usage and form factor.


Figure 40: Stress simulation of Iteration 3.1 in SolidWorks, with a 20 N force applied at the contact points of a single gripper.

Figure 41: Stress simulation of old gripper in SolidWorks, with a 20 N force applied at the contact points of a single gripper

Figure 42: Displacement simulation of Iteration 3.1 in SolidWorks, with a 20 N force applied at the contact points of a single gripper

Figure 43: Displacement simulation of old gripper in SolidWorks, with a 20 N force applied at the contact points of a single gripper

## Comparison with experimental results

When comparing our physical test results to the simulation outcomes, a significant difference in deflection becomes evident (see figure xx). Simulations performed using the same load values applied in the physical tests showed much lower deflection, suggesting that the observed displacement in the real setup is not coming from the grippers alone.
Ideally, we would have performed physical tests on the grippers in isolation to better compare with the simulation data, which was based on the gripper alone (not the full assembly including gears and base). However, due to time constraints, we only tested the full assembled setup and compared that to the gripper-only simulations.
Our observations indicate that the excessive deflection seen in the physical tests is largely caused by movement and flexibility within the base assembly itself (see data appendix 3).


Figure 44: Comparison of deflection between physical tests and SolidWorks simulations for three gripper designs under increasing applied force.
We therefore believe the main reasons for the increased real-world deflection are:
- Low assembly tolerance: Due to sanding and 3D printing imprecision, the base has several small gaps that contribute to overall movement in the system.
- Insufficient structural design for 3D printing: Some parts, such as the gears and base walls, may be too thin or flexible and require design improvements to better resist deformation underload.

Lifetime
The lifetime for gripper 3.1 was determined under a cyclic fatigue test simulation under constant amplitude events with defined cycles. The simulation is Zero Based (LR=0)

meaning that the load varies from zero to a maximum value. Since it wasn’t possible to find reliable fatigue test data (e.g. S/N, Wöhler curve) for PLA, stress amplitude at specific cycles was obtained for PP (Ticona GmbH, 2004, s. 6) as input data for the simulation. Since there are major differences between the mechanical properties of PLA and PP, the results of the test can only serve as a guideline. Since the gripper arm is only submitted to a limited force of 6 N, there is no damage after 1.000.000 cycles (see figure xx). 1.000.000 cycles are considered the minimum lifetime, since this approximately corresponds to daily operation of 1000 sample plates over 3 years.


Figure 45: Fatigue simulation at 1.000.000 cycles.
Even though the simulations suggest there is no damage, it is however considered that some damage will occur, due to e.g. operation and cleaning (which potentially can contain dissolving chemicals). Furthermore, the actual gripping zone will have softer material with higher friction coefficient e.g. rubber that will be worn quicker and should be replaced regularly to secure proper gripping.
In conclusion comparable and reliable test data is needed to make valid assumptions regarding fatigue of the actual gripper based on simulations. Therefore, this would have to be investigated further to make any valid conclusions. These results, however, serve as an indicator that the assumption: that the low force applied to the gripper will not result in major fatigue damage over the minimum lifetime set to 3 years.

## Evaluation of metric

Table 5: Metrics
The gripper is compatible with the existing 3D printed robot arm. The gripper attaches to the robot arm with two bolts and two nuts. The gripper arms are easily attachable with 3 bolts and 3 nuts on each arm and it takes 5 minutes to attach and detach them. The force analysis shows that arms of the gripper are designed in a way that when the force is applied, arms of the gripper do not exceed the yield strength of the material. The whole gripper is made out of 3D printable material with the exception of 2 metal rods. PLA is the material that it was used for 3D printing. Gripper 2.4 is compatible with 50% of the machines in the lab. Gripper 3.2 has a compatibility of 87,5%. That means that this gripper can fit into every machine except Plate hotels. Gripper 3.1 is the best gripper, and it is compatible with every machine in the lab. The gripper lifetime is expected to be 1.000.000 cycles. That means the grippers lifetime is 3 years.

## Proposals for future work

Of the three selected prototypes the most suitable for the application is gripper 3.1. The gripper stays within the setup minimum and target values from the metric. Furthermore, the design is compatible with 100% of the machines from the DALSA lab. The gripper further has a limited deflection of 0,53 mm at the max calculated gripping force with a safety factor of 3. It is however observed that the deflection may derive from the base and not the actual gripper.
A further Finite element analysis of the whole assembly would give a good indication of where the deflection is highest and where the base would need to be thickened just as we did with the simulations for the gripper. This was tried but with the different files the assembly in SolidWorks did not work to make a final mesh. So, with limited time we did not achieve a simulation of everything assembled.
Also, it would be worth looking into a more precise 3D printer with stronger 3D printed material such as carbon fiber reinforced material.

In the rapid prototype process, the base seemed to be a significant challenge during the iteration of the gripper. While the original scope of the project focused on redesigning the gripper. While the original scope of the project focused on redesigning the gripper itself, it quickly became evident that the performance of the gripper was heavily influenced by the base. A considerable amount of time was therefore spent attempting to improve the base to support the new gripper designs. However, due to the limited timeframe and the defined scope of the course, a fully stable and optimized base was not achieved.
It is strongly recommended to further investigate and improve the mechanical design of the base in future work, as this aspect was not fully addressed within the timeframe of the course. If the current mechanical concept is chosen, switching to standard metal gears and gear racks would be recommended. This would likely improve tolerance, increase stiffness, and allow for a thinner design. Enhancing the overall stiffness of the base – either through material upgrades or structural reinforcement – would significantly contribute to a better and more consistent gripper performance.

## References

D.S., P. (n.d.). FRICTION COEFFICIENT OF RUBBER WITH RESPECT TO SOME TYPES OF PLASTICS.
Dalsa frontpage. (n.d.). Retrieved from Dalsa (DTU Arean for Life Science Automation): https://dalsa.dtu.dk/
Deep well plate. (2025). Retrieved from MERCK: https://www.sigmaaldrich.com/DK/en/product/sigma/axypdw10ml24c Gabor, K. (2024). Advancing Laboratory Automation in Life. Kongens Lyngby: DTU, Department of Electrical and Photonics Engineering.
Round bottom assay plate. (2025). Retrieved from MERC: https://www.sigmaaldrich.com/DK/en/product/sigma/axyp96450rcs?utm_source=google&utm_medium=cpc&utm_campaign=21811866450&utm_content=174236308452&gad_source=1&gad_campaignid=21811866450&gbraid=0AAAAAD8kLQTIH6Cp9Dg5OBpimGC8eg3gF&gclid=Cj0KCQjwjdTCBhCLARIsAE Syaefudin, E. A. (2023). The effect of orientation on tensile strenght 3D printing with ABS and PLA materials.
Ticona GmbH. (2004). Integral Hinges in Engineering Plastics. Kelsterbach.
Introduction | Error! Bookmark not defined.
Problem formulation | Error! Bookmark not defined.
Product Design Requirements | Error! Bookmark not defined.
Material selection | Error! Bookmark not defined.
Brainstorm | Error! Bookmark not defined.
First iteration prototype | Error! Bookmark not defined.
Grippers | Error! Bookmark not defined.
Base | Error! Bookmark not defined.
Limitations and improvements (after 1 iteration) | Error! Bookmark not defined.
2nd iteration | 17
Final iteration | Error! Bookmark not defined.
Final iteration gripper: | Error! Bookmark not defined.
Machine capabilities | Error! Bookmark not defined.
Experimental plan with an overview in table form | Error! Bookmark not defined.

Description of experimental procedure | Error! Bookmark not defined.
Results | Error! Bookmark not defined.
Description of theoretical/numerical analysis (Force analysis)...... Error! Bookmark not defined.
For sample plate A | Error! Bookmark not defined.
For sample plate B | Error! Bookmark not defined.
Payload Limitation and Practical Gripping Capacity .....Error! Bookmark not defined.
Force analysis results | Error! Bookmark not defined.
2nd Iterations | Error! Bookmark not defined.
Final Iterations | 34
Comparing with previous gripper | Error! Bookmark not defined.
Comparison with experimental results | Error! Bookmark not defined.
Lifetime | Error! Bookmark not defined.
Evaluation of metric | Error! Bookmark not defined.
Proposals for future work | Error! Bookmark not defined.
Appendix | Error! Bookmark not defined.

## Appendix

Appendix 1: Test setup 1 pictures

Appendix 2: Data test 2, total deflection of assembly

Test gripper 3.1
| Without weights | 100 g | 200 g | 300 g | 400 g | 500 g | 600 g | 700 g | 800 g | 900 g | 1000 g
Distance from fixed point to bottom of gripper | 21,82 | 21,86 | 22,21 | 22,93 | 23,14 | 23,93 | 24,29 | 24,55 | 25,22 | 26 | 26,43
| | 0,04 | 0,39 | 1,11 | 1,32 | 2,11 | 2,47 | 2,73 | 3,40 | 4,18 | 4,61

Test gripper 2.4
| Without weights | 100 g | 200 g | 300 g | 400 g | 500 g | 600 g | 700 g | 800 g | 900 g | 1000 g
Distance from fixed point to bottom of gripper | 24,65 | 24,86 | 25,21 | 25,92 | 26,20 | 26,69 | 27,37 | 27,82 | 28,38 | 28,8 | 29,44
| | 0,21 | 0,56 | 1,27 | 1,55 | 2,04 | 2,72 | 3,17 | 3,73 | 4,15 | 4,79

Test gripper 3.2
| Without weights | 100 g | 200 g | 300 g | 400 g | 500 g | 600 g | 700 g | 800 g | 900 g | 1000 g
Distance from fixed point to bottom of gripper | 23,4 | 24,31 | 24,65 | 25,76 | 26,74 | 27,01 | 27,92 | 28,61 | 29,65 | 30,21 | 31,11
| | 0,91 | 1,25 | 2,36 | 3,34 | 3,61 | 4,52 | 5,21 | 6,25 | 6,81 | 7,71

Appendix 3: Data from simulations and the comparison graph

Weight applied (g) | 100 | 200 | 300 | 400 | 500 | 600 | 700 | 800 | 900 | 1000
Force applied (N) | 1,02 | 2,04 | 3,05 | 4,07 | 5,09 | 6,11 | 7,13 | 8,15 | 9,16 | 10,18
Start distance (mm) | 21,82 | 21,82 | 21,82 | 21,82 | 21,82 | 21,82 | 21,82 | 21,82 | 21,82 | 21,82
End distance after weight (mm) | 21,86 | 22,21 | 22,93 | 23,14 | 23,93 | 24,29 | 24,55 | 25,22 | 26 | 26,43
Deflection (mm) | 0,04 | 0,39 | 1,11 | 1,32 | 2,11 | 2,47 | 2,73 | 3,40 | 4,18 | 4,61
Max deflection from simulation (mm) | 0,09062 | 0,1812 | 0,271 | 0,3616 | 0,4522 | 0,5428 | 0,6334 | 0,724 | 0,8138 | 0,9044
Difference from measurment and simulation (mm) | -0,05 | 0,21 | 0,84 | 0,96 | 1,66 | 1,93 | 2,10 | 2,68 | 3,37 | 3,71
Percent error (%) | 126,55% | 53,54% | 75,59% | 72,61% | 78,57% | 78,02% | 76,80% | 78,71% | 80,53% | 80,38%
Weight applied (g) | 100 | 200 | 300 | 400 | 500 | 600 | 700 | 800 | 900 | 1000
Force applied (N) | 1,02 | 2,04 | 3,05 | 4,07 | 5,09 | 6,11 | 7,13 | 8,15 | 9,16 | 10,18
Start distance (mm) | 24,65 | 24,65 | 24,65 | 24,65 | 24,65 | 24,65 | 24,65 | 24,65 | 24,65 | 24,65
End distance after weight (mm) | 24,86 | 25,21 | 25,92 | 26,20 | 26,69 | 27,37 | 27,82 | 28,38 | 28,8 | 29,44
Deflection from test (mm) | 0,21 | 0,56 | 1,27 | 1,55 | 2,04 | 2,72 | 3,17 | 3,73 | 4,15 | 4,79
Max deflection from simulation (mm) | 0,04575 | 0,09151 | 0,1368 | 0,1826 | 0,2283 | 0,2741 | 0,3198 | 0,3656 | 0,4109 | 0,4566
Difference from measurment and simulation (mm) | 0,16 | 0,47 | 1,13 | 1,37 | 1,81 | 2,45 | 2,85 | 3,36 | 3,74 | 4,33
Percent error (%) | 78,21% | 83,66% | 89,23% | 88,22% | 88,81% | 89,92% | 89,91% | 90,20% | 90,10% | 90,47%
Weight applied (g) | 100 | 200 | 300 | 400 | 500 | 600 | 700 | 800 | 900 | 1000
Force applied (N) | 1,02 | 2,04 | 3,05 | 4,07 | 5,09 | 6,11 | 7,13 | 8,15 | 9,16 | 10,18
Start distance (mm) | 23,4 | 23,4 | 23,4 | 23,4 | 23,4 | 23,4 | 23,4 | 23,4 | 23,4 | 23,4
End distance after weight (mm) | 24,31 | 24,65 | 25,76 | 26,74 | 27,01 | 27,92 | 28,61 | 29,65 | 30,21 | 31,11
Deflection from test (mm) | 0,91 | 1,25 | 2,36 | 3,34 | 3,61 | 4,52 | 5,21 | 6,25 | 6,81 | 7,71
Max deflection from simulation (mm) | 0,2378 | 0,4746 | 0,7111 | 0,9489 | 1,187 | 1,425 | 1,662 | 1,9 | 2,136 | 2,373
Difference from measurment and simulation (mm) | 0,67 | 0,78 | 1,65 | 2,39 | 2,42 | 3,10 | 3,55 | 4,35 | 4,67 | 5,34
Percent error (%) | 73,87% | 62,03% | 69,87% | 71,59% | 67,12% | 68,47% | 68,10% | 69,60% | 68,63% | 69,22%

Physical test of gripper 3.1 (Blue and 8 mm thick)

Physical test gripper 2.4 (Pink and 10 mm thick)

Physical test gripper 3.2 (Grå and 5 mm thick)


Appendix 4: Lab Machines

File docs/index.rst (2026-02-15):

**Bioscara**
============
This is the documentation for Bioscara DIY SCARA robot developed at the **DTU Arena for Life Science Automation (DALSA)**.
See the table of contents below to see the available user guides. 

- The :doc:`getting_started/index` guides help you to install dependencies, build the ROS2 workspace, setup the network and finally operate the robot.
- The :doc:`further_guides/index` guides are targeted towards developers and contain other useful instructions, for example how to build this documentation or flash the joint firmware.
- The :doc:`hardware/index` guides describe the hardware assembly instructions. **Note:** These require a consolidation!
- The :doc:`code/index` links to the C++ API documentation of the ROS2 packages.

The PDF version of this documentation can be found here: :download:`bioscara.pdf <sphinx/latex/latex/bioscara.pdf>`

Architechture
-------------
The control system architecture is schematically displayed in the figure below. The yellow colors whos custom C++ hardware specific code which is described in the :doc:`code/api`. The orange colors are the ROS2 applications for motion control and trajectory generation. The red colors are SiLA applications, not yet implemented as indicated by the dashed lines.



\

.. toctree::
   :maxdepth: 2
   :caption: Contents:

   getting_started/index.rst
   further_guides/index.rst
   hardware/index.rst
   code/index.rst
..

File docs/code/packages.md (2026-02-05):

# ROS2 Package Architecture
The *lib/ros2_ws/src* directory in the ROS2 workspace contains all packages needed to develop, test and operate the Bioscara robot.
Logically coherent software is combined in a package which is useful for distribution and dependecy management.

## Remarks on Nomenclature
- The robot arm (without any gripper) is refered to as the "arm" or "bioscara_arm".
- a custom bioscara gripper is refered to as the "gripper" or "bioscara\_gripper\_\<type\>"
- The assembly of an arm and a gripper is a "robot" or "bioscara\_\<arm\>\_\<gripper\>" .
- An environment with a robot and potentially other objects is a "scene".

## Design goals
The package architecture is designed on modularity, since it is expected future variants of hard- and software will be developed. The modular approach allows to mix and swap old the software. Modularity achieved two fold:

- Standalone packages for arms and grippers.
- Grippers that are simply variants but utilize the same hardware interface, just different hardware description and hardware parameters grouped in a package but with standalone description macros.
- Packages and description macros can be swapped via command line arguments or set in scene specific bringup files.

The architecture may serve as a blueprint for the future integration of more DALSA robots (custom or commercial) into ROS2. 

## Additional MoveIt2 packages
Unfortunately it was necessary to build MoveIt2 from source to use features from the MoveIt Task Constructor, installing MoveIt from source adds many packages to the workspace.
To build the workspace follow the [compilation instructions](building.md).

## Meta Packages
Packages that logically belong together are grouped in meta packages. Meta packages do not contain source code or configuration files but simplify dependency management. For example a hardware meta package may contain the hardware's description, driver, interface, controller and bringup packages. Other packages that depend on that hardware can simply specify the meta package as a dependency and automatically inherit the remaining sub-dependencies. 

The following meta packages are available:

**dalsa_bioscara_arm**: Contains all packages related to the custom bioscara arm hardware component

**dalsa_bioscara_grippers**: Contains all packages related to  the custom bioscara gripper hardware component and its variants. 

**dalsa_controllers**: Contains custom, hardware agnostic controllers.

**dalsa_moveit_configurations**: Contains MoveIt2 configurations.

**system_test_packages**: Contain different simple programs to execute system tests.

## Overview
The diagram below shows a simple package architecture and dependency diagram. It does not yet include the MoveIt configuration package. The individual packages are grouped by their meta package.

```{mermaid}
flowchart TB
 subgraph dalsa_bioscara_arm["dalsa_bioscara_arm"]
        bioscara_arm_bringup["bioscara_arm_bringup"]
        bioscara_arm_description["bioscara_arm_description"]
        bioscara_arm_hardware_interface["bioscara_arm_hardware_interface"]
        bioscara_arm_hardware_driver["bioscara_arm_hardware_driver"]
  end
 subgraph dalsa_bioscara_grippers["dalsa_bioscara_grippers"]
        bioscara_gripper_bringup["bioscara_gripper_bringup"]
        bioscara_gripper_descriptions["bioscara_gripper_descriptions"]
        bioscara_gripper_hardware_driver["bioscara_gripper_hardware_driver"]
        bioscara_gripper_hardware_interface["bioscara_gripper_hardware_interface"]
  end
 subgraph dalsa_controllers["dalsa_controllers"]
        single_trigger_controller["single_trigger_controller"]
  end
  subgraph dalsa_moveit_configurations["dalsa_moveit_configurations"]
        bioscara_arm_gripper_128_moveit_config["bioscara_arm_gripper_128_moveit_config"]
  end
    
    scene_descriptions["scene_descriptions"] --> bioscara_arm_description & bioscara_gripper_descriptions
    scene_bringup["scene_bringup"] --> scene_descriptions & dalsa_bioscara_arm & dalsa_bioscara_grippers & bioscara_rviz_plugin
    bioscara_arm_bringup --> single_trigger_controller & bioscara_arm_description
    bioscara_arm_description --> bioscara_arm_hardware_interface
    bioscara_arm_hardware_interface --> bioscara_arm_hardware_driver
    bioscara_gripper_bringup --> bioscara_gripper_descriptions
    bioscara_gripper_hardware_driver --> bioscara_arm_hardware_driver
    bioscara_gripper_descriptions --> bioscara_gripper_hardware_interface
    bioscara_gripper_hardware_interface --> bioscara_gripper_hardware_driver
    bioscara_rviz_plugin["bioscara_rviz_plugin"] --> dalsa_bioscara_arm & dalsa_bioscara_grippers
    dalsa_motion_plans["dalsa_motion_plans"] --> bioscara_arm_gripper_128_moveit_config 
    bioscara_arm_gripper_128_moveit_config --> scene_bringup
```

## Hardware component package
Hardware component meta packages are structured according to the [RTW Package Structure](https://rtw.b-robotized.com/master/guidelines/robot_package_structure.html) refrence, developed by [dstogl](https://github.com/destogl), a key developer of ros2_control. Each hardware component *dalsa_bioscara_grippers* and *dalsa_bioscara_arm*, i.e. the arm and the gripper have meta package structured as follows, using gripper as an example:
```
dalsa_bioscara_grippers/
├── bioscara_gripper_bringup                                # The bringup package is used to launch a hardware component, either standalone or from another bringup package
│   ├── CMakeLists.txt                                      
│   ├── config                                                                                       
│   │   ├── bioscara_gripper_controller_manager.yaml        # ros2_control controller manager paramters if used stand-alone
│   │   └── bioscara_gripper_controllers.yaml               # Definition of controllers for this hardware component, gripper controller in this case
│   ├── launch                                              
│   │   └── bioscara_gripper.launch.py                      # Use this launch file used to start the component stand-alone, including GUI and ros2_control stack.
│   └── package.xml
├── bioscara_gripper_descriptions                           # The description package contains all files to assemble a component description with Xacro 
│   ├── CMakeLists.txt
│   ├── config                                              
│   │   ├── bioscara_gripper_128_parameters.yaml            # Describes static component parameters parsed in the robot description, like joint limits
│   │   └── bioscara_gripper_<variant_X>_parameters.yaml    # Parameters of another gripper variant
│   ├── launch
│   │   └── view.launch.py                                  # Use this launch file to simple view and inspect the assembled component.
│   ├── meshes                                              # Resources for the URDF file
│   ├── package.xml
│   ├── rviz
│   │   └── display.rviz                                    # Saved display configuration for the stand-alone GUIs
│   └── urdf
│       ├── bioscara_gripper_128.ros2_control               # ros2_control hardware information for the 128 mm variant
│       ├── bioscara_gripper_128.urdf                       # Base URDF file containing kinematic, visual and collision info for the 128 mm variant
│       ├── bioscara_gripper_128.xacro                      # Contains the "load_gripper" macro, combining the .urdf and .ros2control parts for the 128 mm variant
│       ├── bioscara_gripper_<variant_X>.ros2_control       
│       ├── bioscara_gripper_<variant_X>.urdf                       
│       ├── bioscara_gripper_<variant_X>.xacro              # Variants of the gripper using the same hardware interface can be added here
│       ├── materials.xacro
│       └── scene.xacro                                     # bringup/launch file uses this scene for the stand-alone start of the component.
├── bioscara_gripper_hardware_driver                        # The hardware driver contains the hardware specific implementation, like PWM generation for the gripper
│   ├── CMakeLists.txt
│   ├── include
│   │   └── bioscara_gripper_hardware_driver
│   ├── package.xml
│   └── src
│       ├── mBaseGripper.cpp                                # Base implementation
│       ├── mGripper.cpp                                    # Hardware implementation
│       └── mMockGripper.cpp                                # Mock implementation for testing
├── bioscara_gripper_hardware_interface                     # The hardware interface abstracts the hardware driver and creates a hardware componen plugin for ros2_control
│   ├── CMakeLists.txt
│   ├── bioscara_gripper_hardware_interface.xml
│   ├── include
│   │   └── bioscara_gripper_hardware_interface
│   ├── package.xml
│   └── src
│       └── gripper_hardware.cpp
└── dalsa_bioscara_grippers                                 # Meta package
```

The name of the gripper component package is written in plural since it can include multiple variants of the bioscara gripper which use the same hardware interface but might have differen geometries.

### Bringup Packages
The bringup packages inside hardware components contain the ros2_control controller configurations for that specific hardware component, as well as a controller manager configuration if the hardware component is launched stand-alone with the launch file included in the bringup package. Stand-alone launch includes the ros2_control stack and can be used for example hardware interface testing, without having to also start higher level applications like MoveIt.

### Description Packages
Description packages are a core building block of the modular principle. It contains robot description files and control configuration files.
A robot description file is an integral part in many ROS2 applications. ROS2 uses an XML based format called Unified Robot Description File (URDF) which is "*a format to describe the kinematics, dynamics, and geometries of robots, independently of software program*" [[1]][urdf], in detail this includes a systems:

- Kinematic description (joints and frame definitions)
- Visual properties for viszualization
- Collision properties defining physical boundaries for trajectory generation
- Mass and Inertial properties for physical simulation (not utilized in this project)
- The URDF can be expanded for specific applications, in this project it addtionally includes:
- ros2_contol configuration
  - hardware interface plugin
  - command and state interfaces
  - joints
  - gpios

The URDF files can be combined using Xacro, a XML macro extension. With Xacro a virtual robot assembly can be created, allowing to flexibly match and mix hardware components. A desription of the Xacro macros follows in the next section.

The description package also contains a stand-alone *scene* and launch file which can be used to simply display the geometry visuals and collision bodies, test joint limits using joint state broadcaster and frame transformations.

[urdf]: https://vbn.aau.dk/ws/files/710175796/main.pdf	"Understanding URDF: A Dataset and Analysis"

### Dynamic Robot Assembly
The entire robot is assembled in the *scene_descriptions* package, in particular the *load_robot* macro defined in *scene_descriptions/robot.xacro".
The diagram below tries to viszualize the different Xacro macros that make up the robot. The robot can be modified simply either by passing diffferent arguments to the macros, loading different parameters from the paramter files or swapping entire macros. For example the *scene.xacro* file takes a gripper macro path as an argument, thus an entirely different gripper can be loaded as long as it supports the same input arguments. Alternatively one can decide to not mount a gripper at all to the robot by passing an empty gripper macro name.

```{mermaid}
flowchart LR
 subgraph bioscara["bioscara"]
    direction LR
        arm_urdf_param_junction["arm_urdf_param_junction"]
        arm_urdf_origin>"origin"]
        arm_urdf_parent>"parent"]
        arm_urdf_parameters>"parameters"]
        arm_urdf_prefix>"prefix"]
  end
 subgraph bioscara_arm_ros2_control["bioscara_arm_ros2_control"]
    direction LR
        arm_ctrl_param_junction["arm_ctrl_param_junction"]
        arm_ctrl_use_mock_hardware>"use_mock_hardware"]
        arm_ctrl_parameters>"parameters"]
        arm_ctrl_prefix>"prefix"]
  end
 subgraph load_arm["load_arm"]
    direction TB
        arm_param_junction["arm_param_junction"]
        arm_param_file["**[parameters]** = bioscara_arm_parameters.yaml"]
        bioscara
        bioscara_arm_ros2_control
  end
 subgraph bioscara_gripper_128["bioscara_gripper_128"]
        grp_urdf_p[" "]
  end
 subgraph bioscara_gripper_128_ros2_control["bioscara_gripper_128_ros2_control"]
        grp_ctrl_p[" "]
  end
 subgraph load_gripper["load_gripper"]
        grp_param_junction["grp_param_junction"]
        grp_param_file["**[parameters]** = bioscara_gripper_128_parameters.yaml"]
        bioscara_gripper_128
        bioscara_gripper_128_ros2_control
  end
 subgraph load_robot["load_robot"]
    direction TB
        robot_param_junction["robot_param_junction"]
        grp_origin["**[origin]** = xyz=[0 0 0] rpy=[π 0 -π/2]"]
        grp_parent@{ label: "**[prefix]** = 'tool_flange'" }
        load_arm
        load_gripper
  end
 subgraph scene["scene"]
    direction LR
        use_mock_hardware>"**[use_mock_hardware]**"]
        prefix@{ label: "**[prefix]** = ' '" }
        parent@{ label: "**[prefix]** = 'world'" }
        origin["**[origin]** = xyz=[0 0 0] rpy=[0 0 0]"]
        load_robot
  end
 subgraph bus["symbolic multiple parameters"]
        n1["**[target]** = value "] &  n2[" "] --> legend_junction1 ==> legend_junction2 --> n3["target"]
        legend_junction1
        legend_junction2
  end
 subgraph legend["Legend"]
    direction TB
        defined["defined in macro"]
        arg>"macro argument"]
        bus
  end
    arm_ctrl_param_junction --> arm_ctrl_use_mock_hardware & arm_ctrl_parameters & arm_ctrl_prefix
    arm_urdf_param_junction --> arm_urdf_origin & arm_urdf_parent & arm_urdf_prefix & arm_urdf_parameters
    arm_param_junction ==> arm_ctrl_param_junction & arm_urdf_param_junction
    arm_param_file --> arm_urdf_param_junction & arm_ctrl_param_junction
    grp_param_junction ==> bioscara_gripper_128 & bioscara_gripper_128_ros2_control
    grp_param_file --> bioscara_gripper_128 & bioscara_gripper_128_ros2_control
    grp_origin --> grp_param_junction
    grp_parent --> grp_param_junction
    robot_param_junction ==> grp_param_junction & arm_param_junction
    use_mock_hardware --> robot_param_junction
    origin --> robot_param_junction
    prefix --> robot_param_junction
    parent --> robot_param_junction
    arm_urdf_param_junction@{ shape: sm-circ}
    arm_ctrl_param_junction@{ shape: sm-circ}
    arm_param_junction@{ shape: sm-circ}
    arm_param_file@{ shape: manual-input}
    grp_param_junction@{ shape: sm-circ}
    grp_param_file@{ shape: manual-input}
    robot_param_junction@{ shape: sm-circ}
    grp_origin@{ shape: manual-input}
    grp_parent@{ shape: manual-input}
    prefix@{ shape: manual-input}
    parent@{ shape: manual-input}
    origin@{ shape: manual-input}
    defined@{ shape: manual-input}
    legend_junction1@{ shape: sm-circ}
    legend_junction2@{ shape: sm-circ}

    style load_arm fill:#FFD600
    style load_gripper fill:#00C853
    style load_robot fill:#C8E6C9
    style scene fill:#FFE0B2
```

After assembling the bioscara robot in its default state the following kinematic chain is created:

```{mermaid}
flowchart LR
 subgraph arm["arm"]
        base_link["base_link"]
        link_1["link_1"]
        link_2["link_2"]
        link_3["link_3"]
        link_4["link_3"]
        tool_flange["tool_flange"]
  end
 subgraph gripper["gripper"]
        grp_base_link["grp_base_link"]
        left_jaw_link["left_jaw_link"]
        right_jaw_link["right_jaw_link"]
        tool["tool"]
  end
 subgraph robot["robot"]
        arm
        gripper
  end
 subgraph scene["scene"]
        robot
        world["world"]
  end
    tool_flange -- origin --> grp_base_link
    grp_base_link --> left_jaw_link & right_jaw_link & tool
    base_link -- j2 --> link_1
    link_1 -- j2 --> link_2
    link_2 -- j3 --> link_3
    link_3 -- j4 --> link_4
    link_4 -- flange_joint --> tool_flange
    world -- origin --> base_link

    style arm fill:#FFD600
    style gripper fill:#00C853
    style robot fill:#C8E6C9
    style scene fill:#FFE0B2
```
## Root Level Scene Packages

### Scene Description
The main *scene.xacro* file describes the robot and its environment, in this case a table top. It loads the *load_robot* macro defined in the *robot.xacro* file. The resulting robot has been described in the [Robot Assembly section](#dynamic-robot-assembly).

## Scene Bringup
Contains the launch files of a specific robot configuration. 

:::{tip}
This package contains the main launch file to start a robot configuration including the ros2_control stack using the *\<RobotConfiguration\>.launch.py* launch file.
Start Bioscara with the currently mounted 128 mm gripper, execute `ros2 launch scene_bringup bioscara_arm_gripper128.launch.py use_mock_hardware:=true/false gui:=true/false`.
:::

:::{note}
This launch files might be superseeded by a single launch file that additionally launches the MoveIt move_group from a hardware specific dalsa_moveit_configurations package.
:::

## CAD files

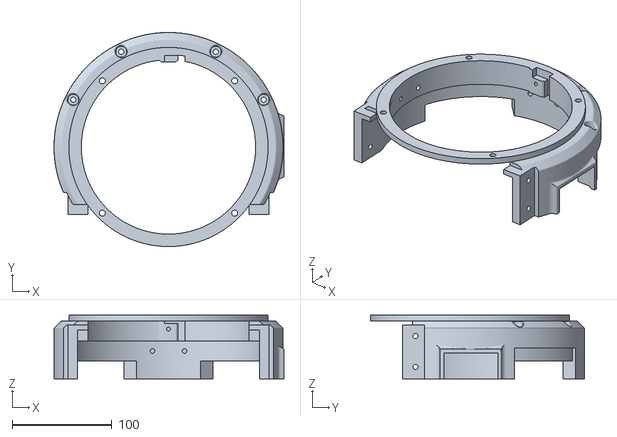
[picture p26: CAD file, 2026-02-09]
hardware/meshes/base_link/Robot base main body.stl
231.0 x 215.0 x 64.0

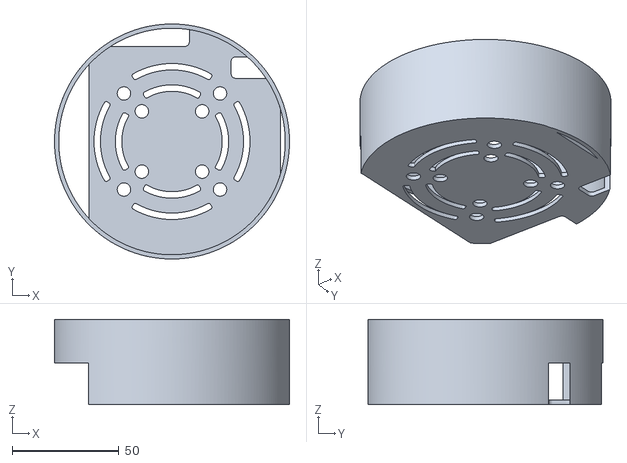
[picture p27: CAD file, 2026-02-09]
hardware/meshes/base_link/Cable box.stl
110.0 x 110.0 x 40.0

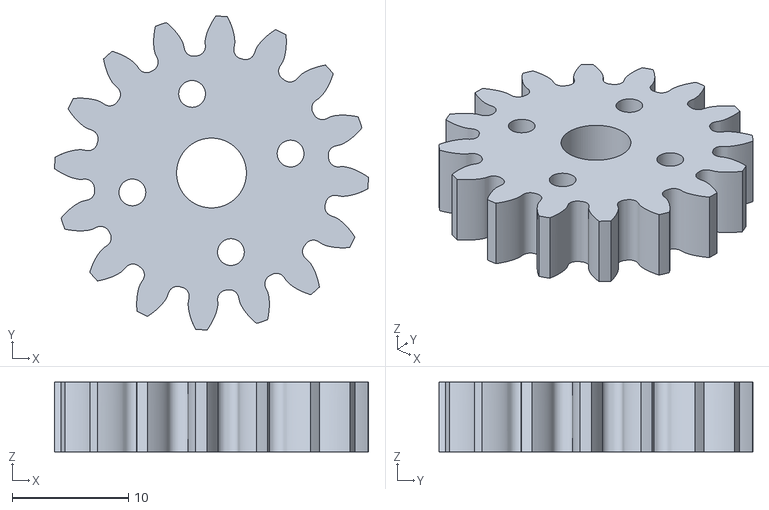
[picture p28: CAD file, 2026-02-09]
hardware/meshes/gripper_v1/Spur gear 16T.stl
27.0 x 27.0 x 6.00

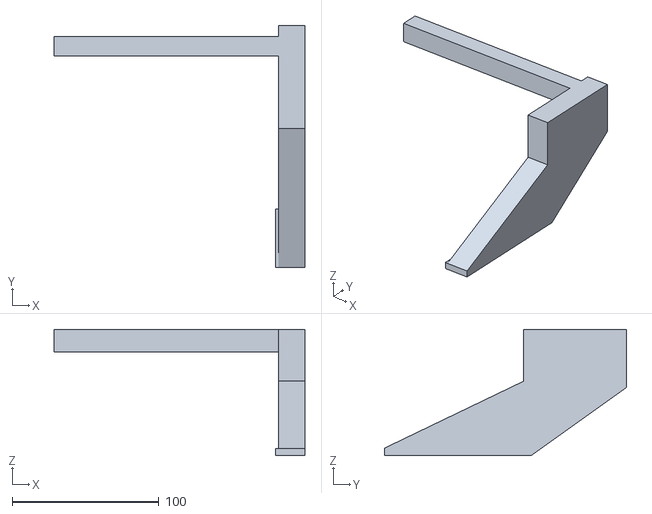
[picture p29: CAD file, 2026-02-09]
hardware/meshes/gripper_v2_primitive/left_jaw.stl
170.9 x 165.1 x 85.9

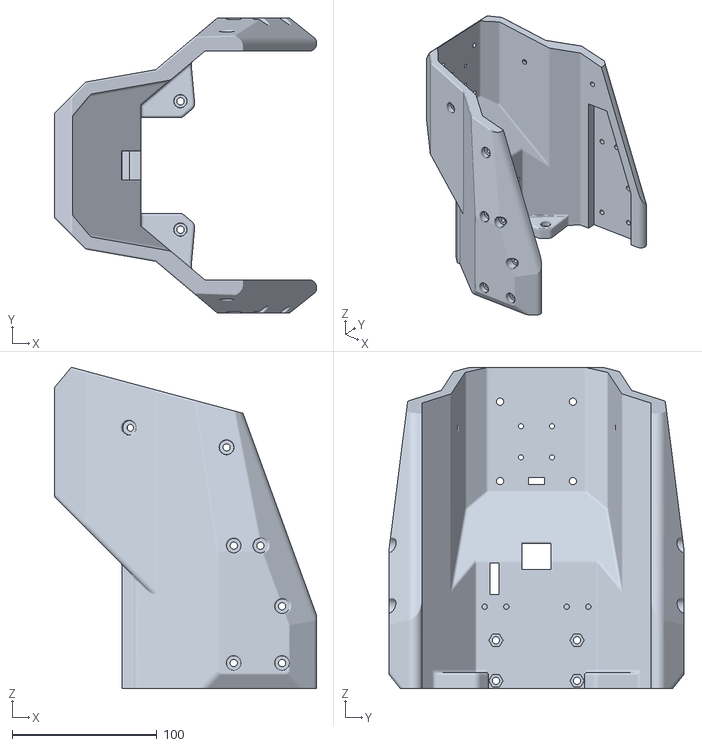
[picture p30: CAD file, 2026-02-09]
hardware/meshes/link_1/Bottom shell.stl
181.2 x 204.0 x 221.6

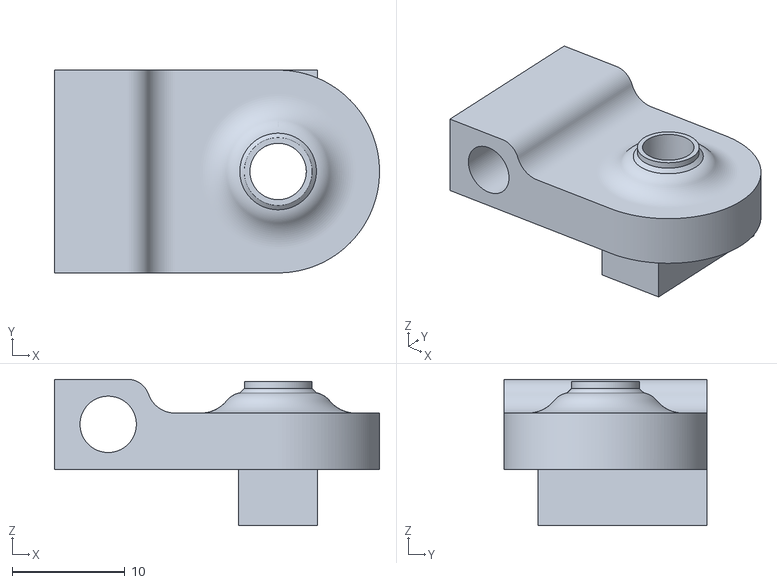
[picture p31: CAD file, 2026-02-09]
hardware/meshes/link_2/Mount 1 for belt tensioner 2.stl
28.9 x 18.0 x 13.0

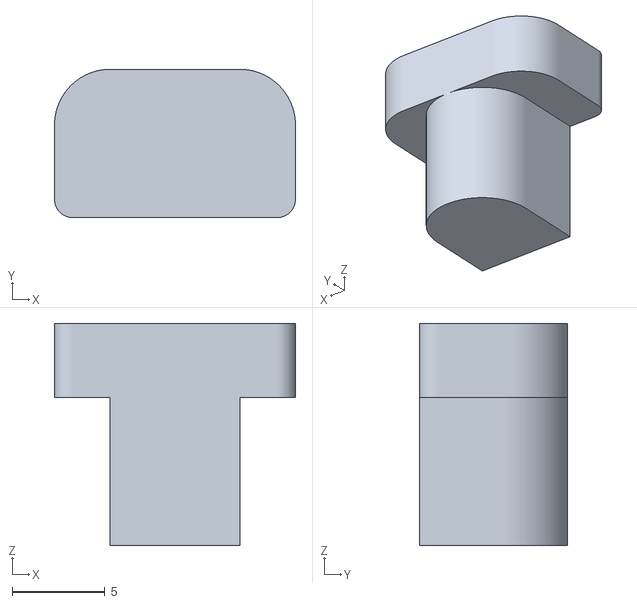
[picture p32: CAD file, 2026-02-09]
hardware/meshes/link_3/tensioner_stop_block.stl
13.0 x 8.00 x 12.0

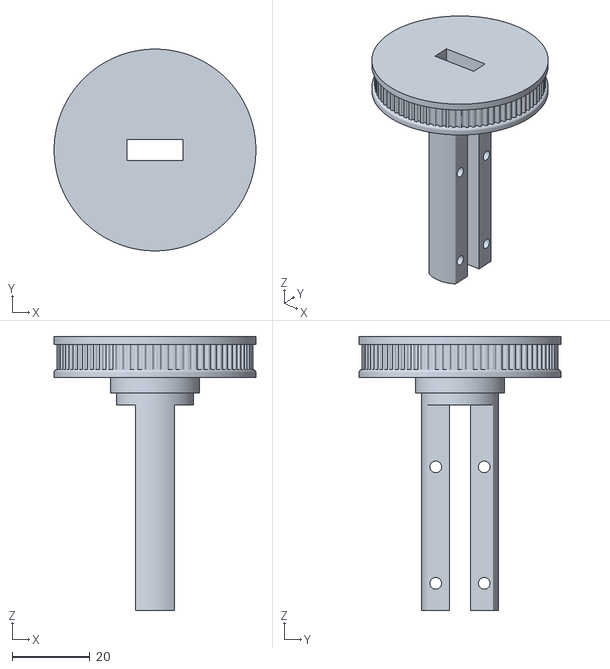
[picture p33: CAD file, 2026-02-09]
hardware/meshes/link_4/80T gear.stl
52.0 x 52.0 x 70.6

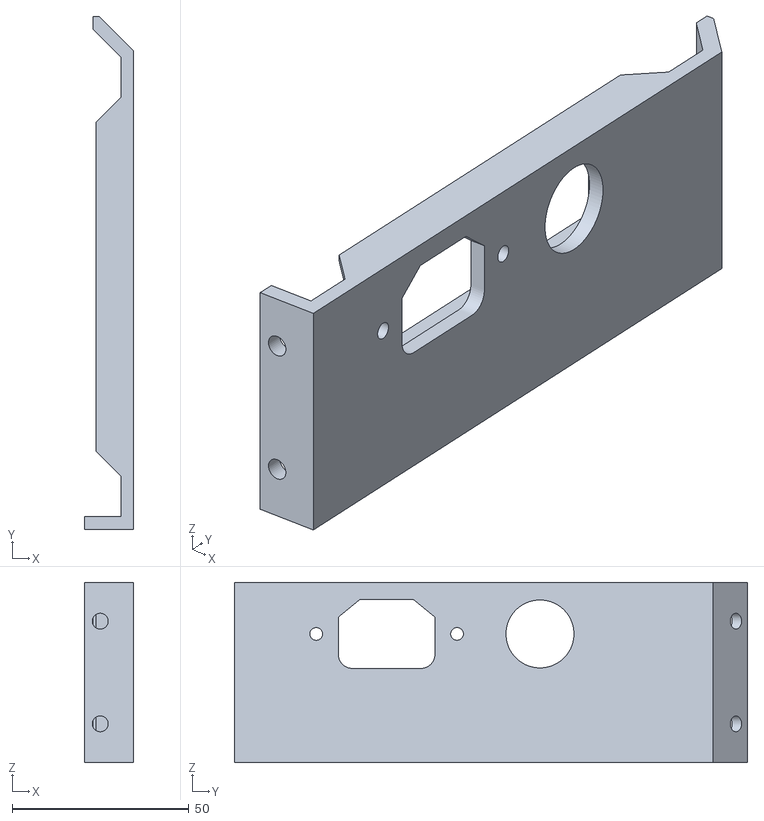
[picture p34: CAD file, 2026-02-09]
hardware/meshes/base_link/PSU box front.stl
13.8 x 145.0 x 51.0

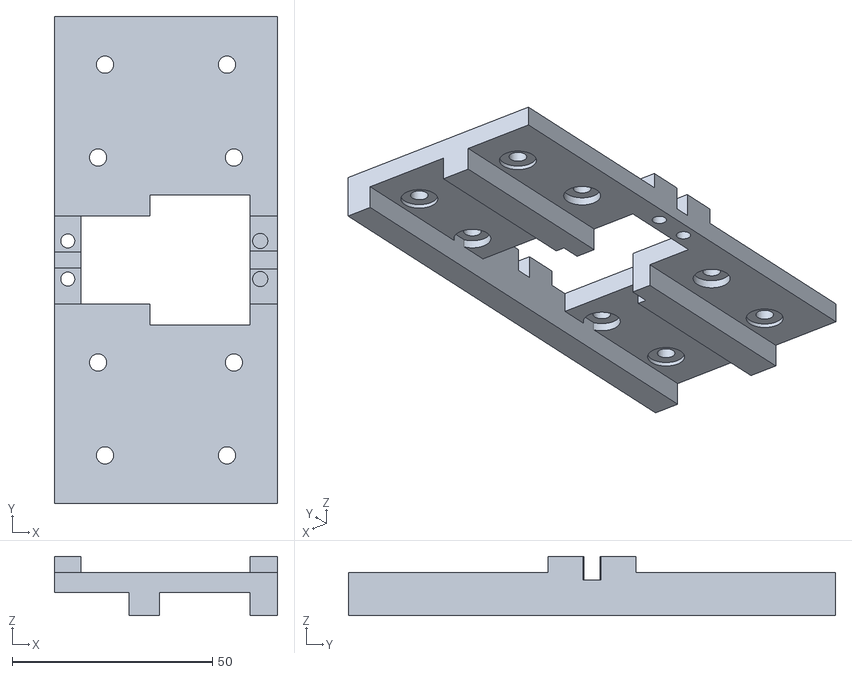
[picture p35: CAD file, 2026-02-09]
hardware/meshes/gripper_v1/Gripper base.stl
55.7 x 121.5 x 14.8

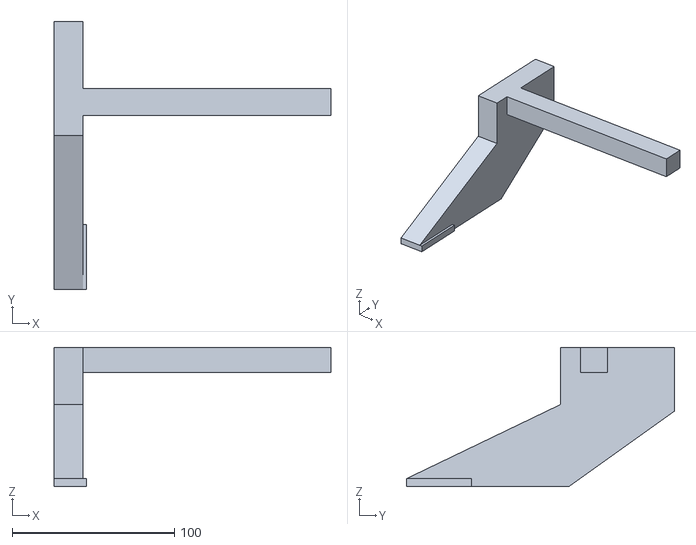
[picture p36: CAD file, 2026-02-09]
hardware/meshes/gripper_v2_primitive/right_jaw.stl
170.9 x 165.1 x 85.9

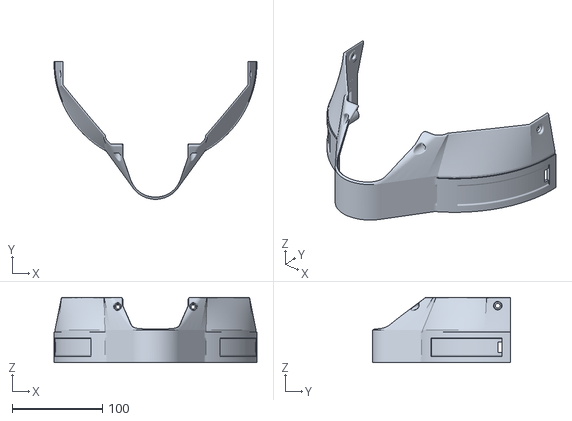
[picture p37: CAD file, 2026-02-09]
hardware/meshes/link_1/Cover 1.stl
224.5 x 152.3 x 72.0

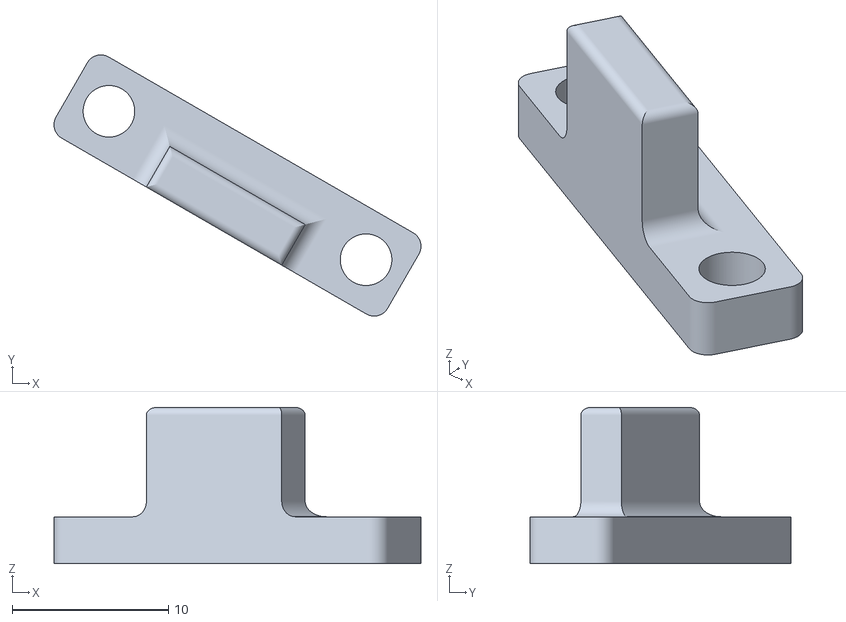
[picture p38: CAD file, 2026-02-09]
hardware/meshes/link_2/J3_endstop_l.stl
23.5 x 16.7 x 10.0

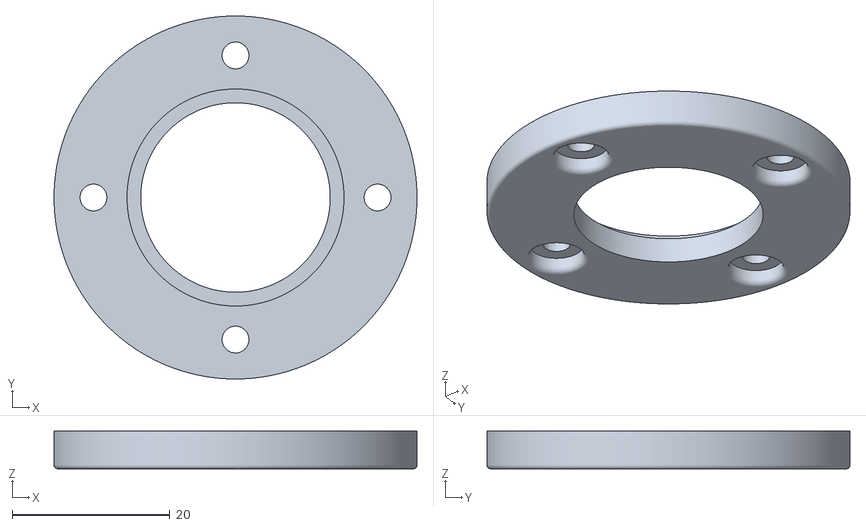
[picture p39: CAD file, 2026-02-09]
hardware/meshes/link_3/BB bottom mount.stl
46.0 x 46.0 x 4.80

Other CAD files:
hardware/meshes/link_4/J4 roller.stl
hardware/meshes/base_link/Bottom cover.stl
hardware/meshes/gripper_v1/Right claw mount.stl
hardware/meshes/gripper_v2_primitive/base.stl
hardware/meshes/base_link/Electronics cover v2.stl
hardware/meshes/base_link/J1_endstop.stl
hardware/meshes/base_link/Leg 1.stl
hardware/meshes/base_link/Leg 2.stl
hardware/meshes/base_link/PSU box v2.stl
hardware/meshes/base_link/PSU cover.stl
hardware/meshes/base_link/PSU rear wall.stl
hardware/meshes/base_link/Rear leg.stl
hardware/meshes/base_link/Spur Gear (140 teeth).stl
hardware/meshes/base_link/switch_faceplate_adapter.stl
hardware/meshes/gripper_v1/Left claw mount.stl
hardware/meshes/gripper_v1/Left gripper mount.stl
hardware/meshes/gripper_v1/Left mount.stl
hardware/meshes/gripper_v1/Left rack gear.stl
hardware/meshes/gripper_v1/Right gripper mount.stl
hardware/meshes/gripper_v1/Right mount.stl
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

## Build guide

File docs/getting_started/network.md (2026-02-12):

# Network Setup
This document describes the network architecture and possibilities to establish inter-device connections.

## Architecture
If the network configuration described in the [installation instructions](installation.md) are followed, then the robot controller and control PC are set-up for the network architecture as follows:

```{mermaid}
graph TD;
subgraph Wifi["Wifi"];

laptop["Laptop
hostname: -"]

DTUsecure["DTUsecure

hostname: -"]:::wifi

laptop<-."IP: 10.209.X.X".->DTUsecure

end
subgraph LAN["LAN"];

robot["Raspberry Pi 
hostname: scara"];

dev["Control PC
hostname: scara-dev"];

Switch<--IP: 10.10.10.3-->dev
Switch<--IP: 10.10.10.2-->robot

end

Switch<--"(optional) 
IP: 10.10.10.4"-->laptop
dev<-."(optional)
IP: 10.209.X.X".->DTUsecure
robot<-."(optional)
IP: 10.209.X.X".->DTUsecure
dev<-."(optional)
IP: 192.168.137.X".->laptop
robot<-."(optional)
IP: 192.168.137.X".->laptop

classDef wifi stroke:#f00
classDef bar stroke:#0f0
classDef foobar stroke:#00f
```

The Laptop is optional, but useful during development. In case a Windows hotspot is used the IP addresses are 192.168.137.X (Subnetmask 255.255.255.0).

## Permanent Ethernet LAN
If only the control PC and the robot controller are in the network, the switch can be omitted and the devices connected directly to each other via an Ethernet cable. The devices should see each other on their respective IP adress.

:::{note}
Although this should work in theory, it has not been tested yet. A third developer PC has always been connected and a switch employed.
:::

If a third device needs to join the network, a network switch is needed to route the trafic.

## Temporary WiFi Connection
Both the robot controller and control PC should be configured to automatically connect to a WiFi network with the the following credentials:  
**SSID**: DALSA_IOT  
**Password**: dalsa_iot

It is possible to gain access wirelessly by creating such an access point. An easy solution is a smartphone or laptop WiFi hotspot.
In the hotspot's settings the IP adress of the connected device will show up if it has sucessfully connected.

## Semi-Permanent Internet Access through DTUsecure
There are two options to access the internet. 

### Through the temporary WiFi AP
Create the access point as described in the previous section, and the device will have internet access forwarded via the hotspot. This method is simple, yet the internet connection is slow and unstable. Not ideal to pull a large repository from Github for example.

### Via DTUsecure
Connect the device to the DTUsecure WiFi network.

The easiest way is to simply execute the connection script *installation/scripts/connect_DTUsecure.sh*:

If the robot should be connected to DTUsecure, for example for a faster connection, run the provided script *installation/scripts/connect_DTUsecure.sh*. DTUsecure uses the WPA-EAP authethication mechanism with your DTU id and DTU password. The script has been made to simplify the setup.

:::{caution}
Due the nature of the OS, your DTU accounts password will be saved in plain text in a netplan file on the system if the connection shall be saved persistently betweeen reboots! Follow the scripts output to see where.
:::

then the script can be run simply by invoking:
```bash
sudo bash installation/scripts/connect_DTUsecure.sh
```
The script adds a connection via nmcli, and asks the user for DTU id and password and if the credentials should be saved.

## Further Information
Managing networks on Linux can be confusing, for example if interfaces show up as 'unmanaged' the chances are high that a different network manager has control over the interface. [This](https://wiki.archlinux.org/title/Network_configuration#Network_managers) table gives a good overview which programs might be involved.
Note that Netplan is not mentioned there, since Netplan only takes a standardized configuration file as input and then depending on the renderer creates the configuration for the backend. Currently Netplan only works with systemd-networkd and NetworkManager, the latter is much simpler to use with its CLI `nmcli`, and terminal UI `nmtui`.

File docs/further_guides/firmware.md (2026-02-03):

# Modifying and Flashing the Joint Firmware
The joint firmware is programmed in C++ using the Arduino framework since the uStepperS32 stepper library is released for that ecosystem.

## Prerequisites
In order to flash firmware to the uStepperS32 stepper controllers some prerequisites must be met. The following guide is copied for reference from the [uStepper website](https://www.ustepper.com/getting-started-with-ustepper/).

### Install the Arduino IDE
Installing the uStepperS32 library and flashing the firmware is done through the Arduino IDE which needs to be installed on the developer's computer from [here](https://www.arduino.cc/en/software/).

### Install STM32 CUBE Programmer
The uStepper is based on an STM32F401 microcontroller. The STM32 CUBE Programmer is used behind the scenes to flash the firmware from the Arduino IDE.
Install the programmer from [here](https://www.st.com/en/development-tools/stm32cubeprog.html).

### Add the uStepperS32 library to the Arduino IDE
In the Arduino IDE, go to *File*->*preferences* and append the URL `https://raw.githubusercontent.com/uStepper/uStepperSTM32Hardware/master/package.json` to the Additional Boards Manager URLs field at the bottom and accept with OK.

Then install the uStepper board through the board manager under *Tools*->*Board*->*Boards Manager*. Search for "ustepper" and the board should show up after the board manager has refreshed. Then press INSTALL.

Finally it should now be possible to select the uStepper STM32 boards under *tools*->*boards*.
        
### Install the uStepperS32 Library
Go to *Sketch*->*Include Library*->*Manage Libraries*, search for “uStepperS32”, and press INSTALL.
Now both the hardware and the library are setup for compilation and flashing.

## Flashing the Firmware
To flash the firmware on the uStepper board, open the *lib/joint_firmware/joint/joint.ino* firmware file with the Arduino IDE, connect the uStepper board with a USB-C cable to the computer, select the correct serial port and the board as "uStepper STM32 boards" under the "board and port" tab. 

The follow the steps to flash the firmware:
1. Press and hold the BOOT button on the uStepper board
2. Keep the BOOT button is pressed and press the RESET button for at least 0.5 s
3. Release the BOOT button
4. Select UPLOAD in the Arduino IDE. The board is now in dowload mode and will load the new firmware.

Monitor the Arduino IDE output console for potential error messages.

## Other Notes
The buttons on the uStepper board are very difficult to reach on J2 if it is mounted on the robot. A thin non-conductive stick can be used to press the BOOT button, the RESET button should be reachable by hand.

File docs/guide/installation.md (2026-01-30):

## Installing 

<!-- Merge dev_machine and Raspberry Pi Readme here -->

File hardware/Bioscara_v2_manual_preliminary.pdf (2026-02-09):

# BIO SCARA MANUAL v2

February 2026

# NOTE:

# This User Guide is largly based on Bioscara v1 and hence not most 3D graphics, assembly instructions and print guides are not yet updated

# PROPOSAL

## STRUCTURE REINFORCEMENT

The overall mechanical structure should be reinforced with light-weight rigid parts (such as metal or carbon-fiber tubes). This should reduce the arm’s flexibility which should also reduce the end-effector’s vibrations. As an example, consider the same arm structure but with holes parallel to the arm. These would be designed for the insertion of rods of tubes.
These would improve the mechanical properties of the arm in the weakest point.
Of course, the flexibility will always remain in the parts where the arm links are connected through joints (for example due to the reliance on timing belts) but it should be to a smaller extent.

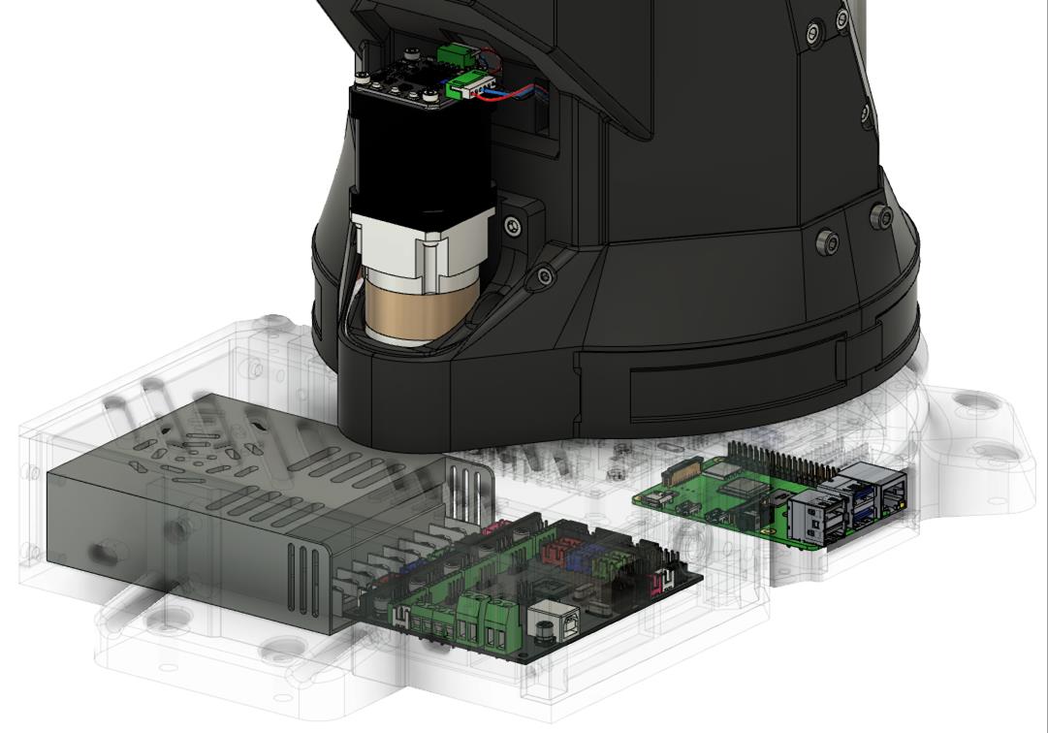
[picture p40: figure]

POWER SUPPLY The robot uses no more than 30% of the maximum possible output power (400W), therefore it is possible to use a smaller and cheaper power supply which also results in a more compact design. A 100W power supply is enough to power all actuators and electronics however one should consider the specific application in which the robot will be used. This includes considerations on what end-effector will be used and if other peripherals will be

powered from the robot’s power supply.

## Using a more compact power supply would result in more

available space left for the electronics where for example,

## a control board could be placed to improve the cable

management of joint 1.

## GRIPPER

The robot can be equipped with various gripper types or devices. In the initial application, the gripper is responsible for pick and place tasks of well plates and that is why the gripper tries to mimic the standard grippers used in the bio industry however while utilizing only off the shelf components.

Standardization of well plates follows the ANSI/SLAS Microplate Standards. For this project, the main aspects of these standards included the ANSI/SLAS 12004 for footprint dimensions, ANSI/SLAS 22004 for height dimensions, and ANSI/SLAS 42004 for well positions. Such standardization ensures compatibility with a range of automated laboratory equipment. The standardized footprint for microplates is 127.76 mm by 85.48 mm, with a tolerance of ± 0.5 mm. It is important to note that while the footprint and well positions of these plates are standardized, the height dimension and number of wells can vary. This variation comes from different volumes the plates are designed to hold and the specific designs of the wells

By building a prototype, It was determined that having a strictly 3D printed gripper is not feasible. Various materials have been used, ranging from a typical PLA to much stronger materials like PA CF. By doing several iterations and building multiple prototypes, it has been concluded that building a gripper made out of both plastic and metal is the suitable solution.

## Note:

The gripper design still has a lot of room for improvements, with the main focus on making the gripper more compact, rigid as well as to increase its strength.

# PARTS LIST

SCREWS, NUTS,

## WASHERS

M5

NUTS
87x M5 NUT

WASHERS
13x M5 WASHER

SCREWS
5x M5X100
1x M5X75
4x M5X50
2x M5X45
2x M5X40 FLAT
HEAD
4x M5X40
3x M5X35 FLAT
HEAD
3x M5X30 FLAT
HEAD
6x M5X30
32x M5X20
44x M5X15
10x M5X10

M4

NUTS
44x M4 NUT

WASHERS
2x M4 WASHER

SCREWS
3x M4X70
4x M4X40
1x M4X30
4x M4X20
18x M4X15
38x M4X10
4x M4X8 FLAT
HEAD
5x M4X8

M3

NUTS
33 M3 NUT

WASHERS
4 M3 WASHER

SCREWS
8x M3X30
4x M3X20
4x M3X10 FLAT
HEAD
52x M3X10
29x M3X8
9x M3X6

M2

NUTS
33 M3 NUT

WASHERS
4 M3 WASHER

SCREWS
4x M2x6

# 3D PRINTING

## 3D PRINTER Parts have been printed on a Bambulab P1S printer. This printer has a print volume of

25dm^3. This volume is required for some bigger parts of the robot base and joint 1.

## FILAMENT The parts have been manufactured from PLA and PETG. It has been estimated that around 4kg of filament is required (1kg of PLA and 3kg of PETG but this ratio depends

on the user’s choice of filament where the filament type could be either of those.

## MODELS STL files have been added A complete Fusion360 model can also be found on github MANUFACTURING The following slides illustrate the suggested print parameters for each model as well as the correct print orientation. Of course, multiple parts can be printed at once to reduce

overall print time .

## Bottom cover

Print parameters: • Material: PETG • Layer height:

0.2mm
- Infill: 15% • Wall loops: 2

## Cable box

Print parameters: • Material: PETG • Layer height:

0.2mm
- Infill: 15% • Wall loops: 2

Note:
Support is required

## Electronics cover

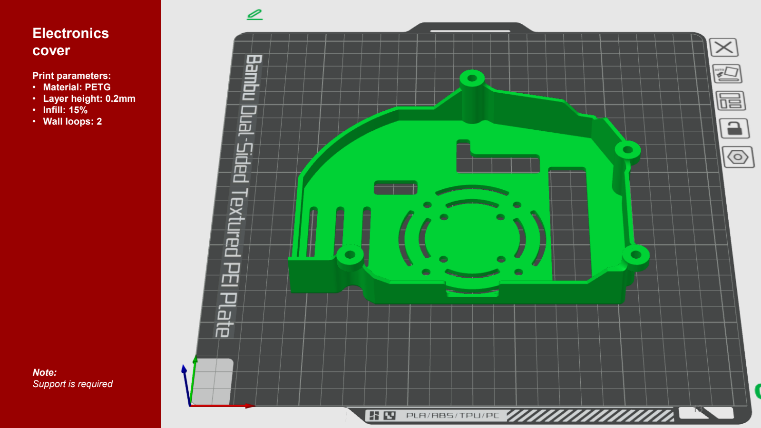
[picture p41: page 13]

Print parameters: • Material: PETG • Layer height: 0.2mm • Infill: 15% • Wall loops: 2

Note:
Support is required

## Leg 1&2

Print parameters: • Material: PETG • Layer height:

0.2mm
- Infill: 20% • Wall loops: 4

## PSU front panel

Print parameters: • Material: PETG • Layer height:

0.2mm
- Infill: 20% • Wall loops: 4

## PSU box

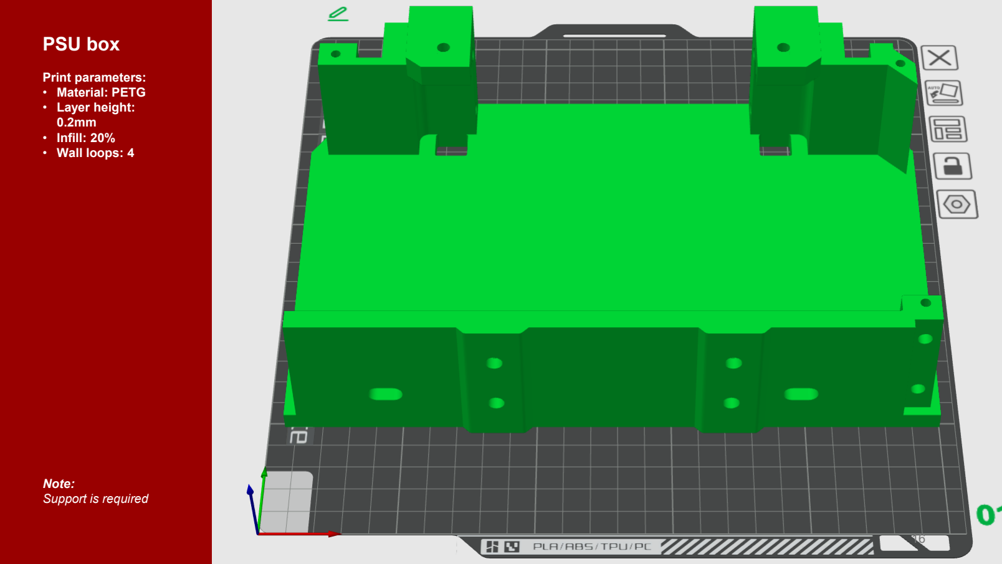
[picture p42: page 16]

Print parameters: • Material: PETG • Layer height:

0.2mm
- Infill: 20% • Wall loops: 4

Note:
Support is required

## PSU cover

Print parameters: • Material: PETG • Layer height:

0.2mm
- Infill: 15% • Wall loops: 2

## PSU rear wall

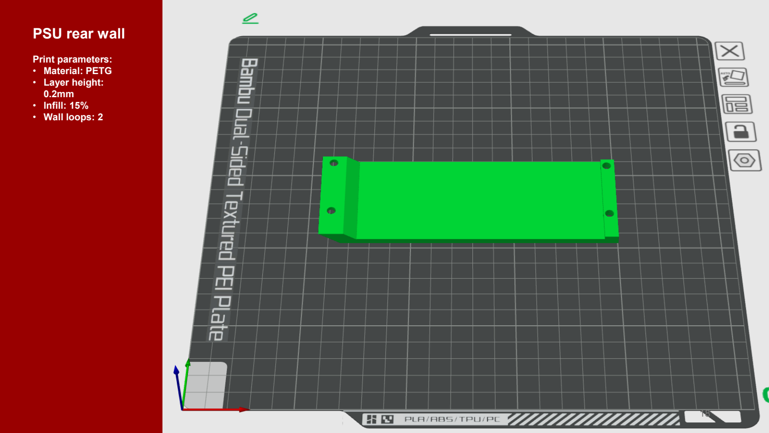
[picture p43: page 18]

Print parameters: • Material: PETG • Layer height:

0.2mm
- Infill: 15% • Wall loops: 2

## Rear leg

Print parameters: • Material: PETG • Layer height:

0.2mm
- Infill: 20% • Wall loops: 4

## Robot base body

Print parameters: • Material: PETG • Layer height: 0.2mm • Infill: 20% • Wall loops: 4

Note:
Support is required

## Spur gear

140T

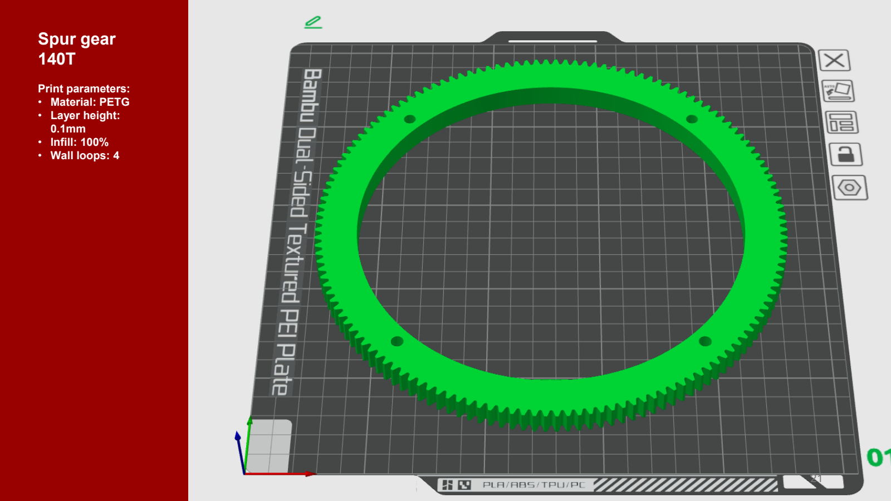
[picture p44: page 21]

Print parameters: • Material: PETG • Layer height:

0.1mm
- Infill: 100% • Wall loops: 4

## Shell mount

Print parameters: • Material: PETG • Layer height:

0.2mm
- Infill: 20% • Wall loops: 4

## J1 base

Print parameters: • Material: PETG • Layer height:

0.2mm
- Infill: 20% • Wall loops: 4

Note:
Support is required

## Bottom shell

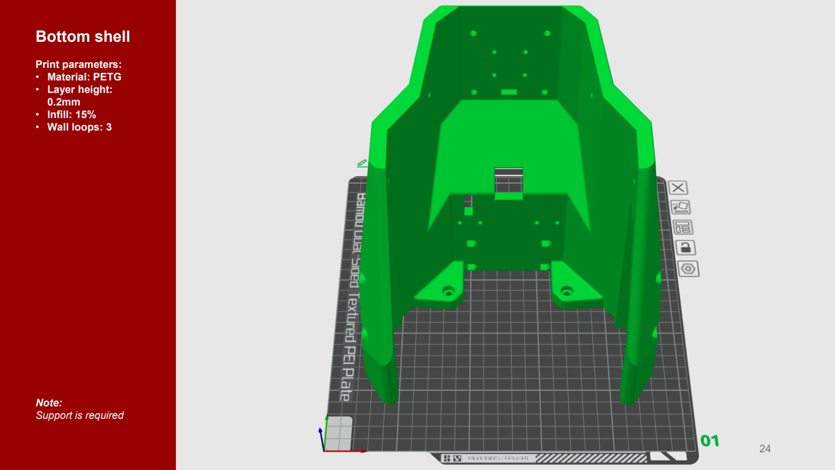
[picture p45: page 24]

Print parameters: • Material: PETG • Layer height:

0.2mm
- Infill: 15% • Wall loops: 3

Note:
Support is required

## Rear cover

Print parameters: • Material: PETG • Layer height:

0.2mm
- Infill: 15% • Wall loops: 2

Note:
Support is required

## Front cover

Print parameters: • Material: PETG • Layer height:

0.2mm
- Infill: 15% • Wall loops: 2

Note:
Support is required

## Spur gear 20T

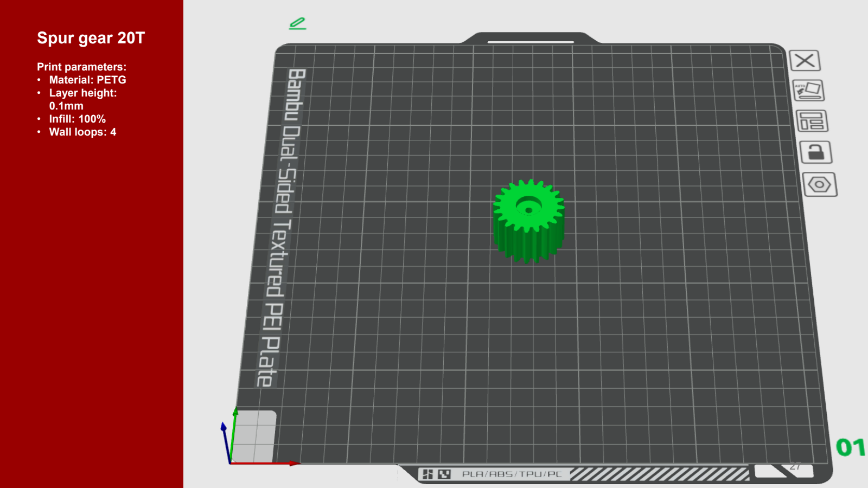
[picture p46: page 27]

Print parameters: • Material: PETG • Layer height:

0.1mm
- Infill: 100% • Wall loops: 4

## M1 mount

Print parameters: • Material: PETG • Layer height:

0.2mm
- Infill: 20% • Wall loops: 4

## Middle shell

Print parameters: • Material: PETG • Layer height:

0.2mm
- Infill: 15% • Wall loops: 3

Note:
Support is required

## Top cover

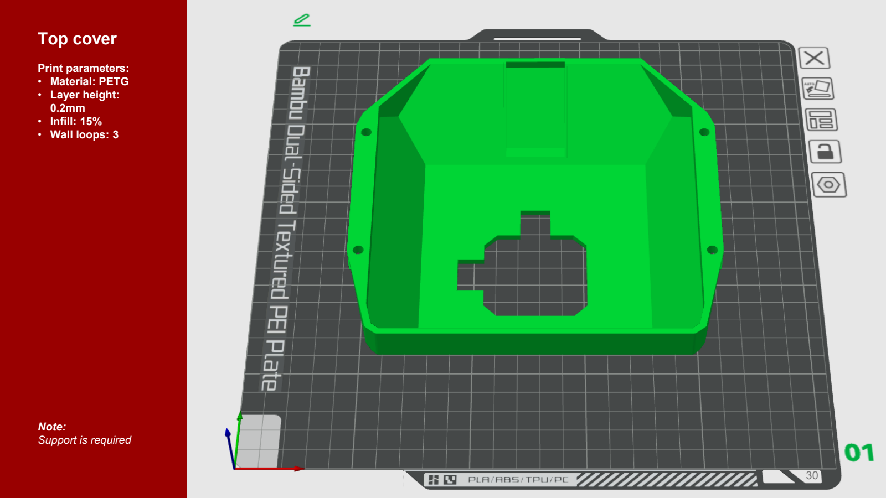
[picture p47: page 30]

Print parameters: • Material: PETG • Layer height:

0.2mm
- Infill: 15% • Wall loops: 3

Note:
Support is required

## Top mount

Print parameters: • Material: PETG • Layer height:

0.2mm
- Infill: 20% • Wall loops: 4

Note:
Support is required

## Bottom shell

Print parameters: • Material: PETG • Layer height:

0.2mm
- Infill: 15% • Wall loops: 3

Note:
Support is required

## J1 cable holder

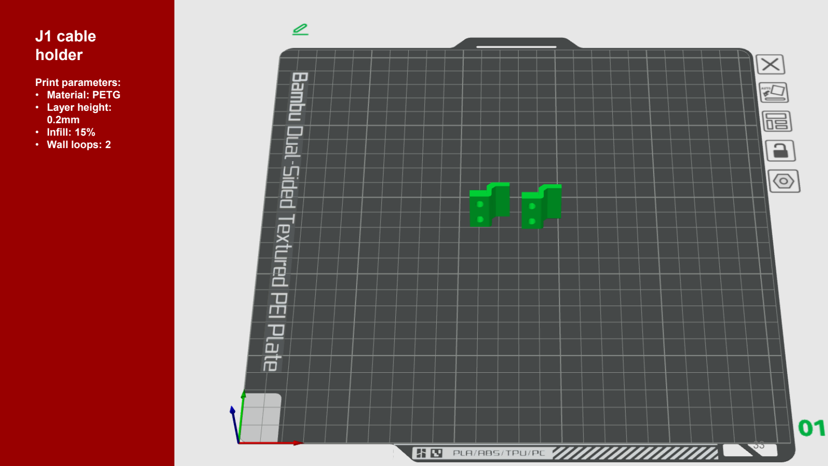
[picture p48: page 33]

Print parameters: • Material: PETG • Layer height:

0.2mm
- Infill: 15% • Wall loops: 2

## Cover clip 1&2

Print parameters: • Material: PETG • Layer height:

0.2mm
- Infill: 15% • Wall loops: 2

## Logo

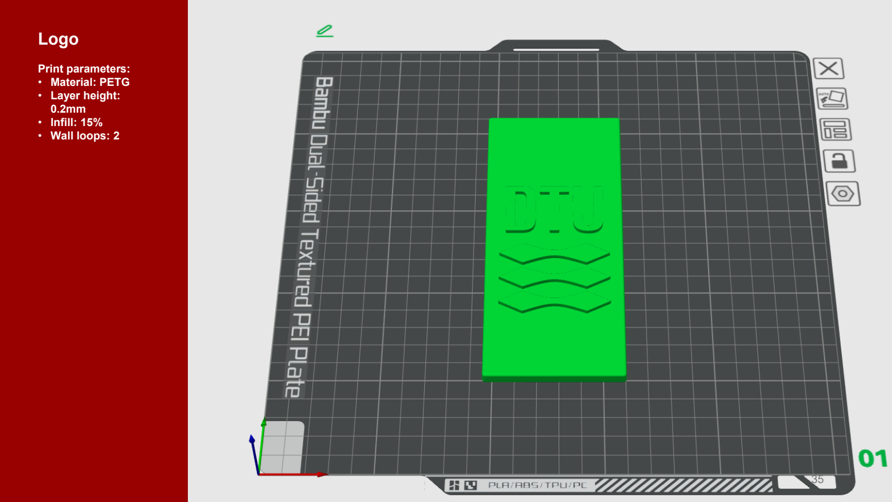
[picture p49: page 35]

Print parameters: • Material: PETG • Layer height:

0.2mm
- Infill: 15% • Wall loops: 2

## J1 sensor trigger

Print parameters: • Material: PETG • Layer height: 0.2mm • Infill: 20% • Wall loops: 4

## Arm link top

Print parameters: • Material: PETG • Layer height:

0.2mm
- Infill: 20% • Wall loops: 4

Note:
Support is required

## Arm link bottom

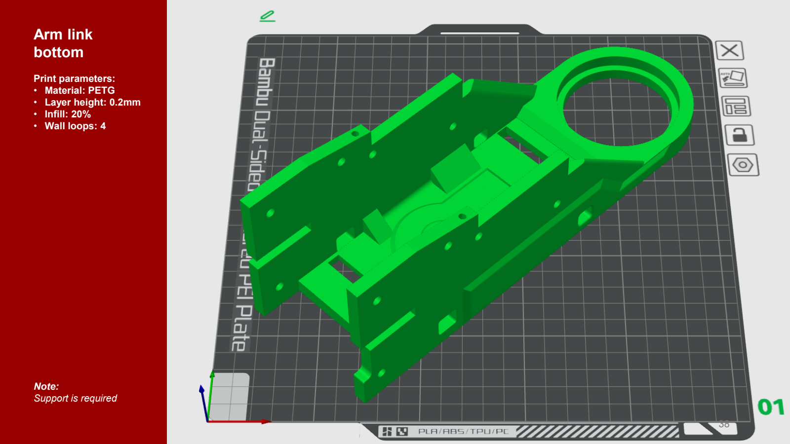
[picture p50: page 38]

Print parameters: • Material: PETG • Layer height: 0.2mm • Infill: 20% • Wall loops: 4

Note:
Support is required

## Arm mount

Print parameters: • Material: PETG • Layer height:

0.2mm
- Infill: 20% • Wall loops: 4

Note:
Support is required

## Gear 25T &

96T

Print parameters: • Material: PETG • Layer height:

0.1mm
- Infill: 100% • Wall loops: 4

## Arm cover

1&2

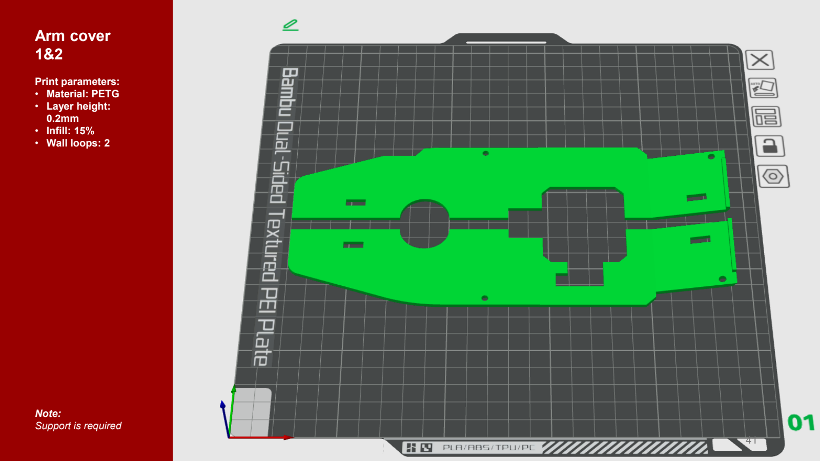
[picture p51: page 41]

Print parameters: • Material: PETG • Layer height:

0.2mm
- Infill: 15% • Wall loops: 2

Note:
Support is required

## J2 Cable holder

Print parameters: • Material: PETG • Layer height:

0.2mm
- Infill: 15% • Wall loops: 3

## J2 Cover clip

1&2

Print parameters: • Material: PETG • Layer height: 0.2mm • Infill: 15% • Wall loops: 2

## J2 Belt tensioner 2

1&2&3&4

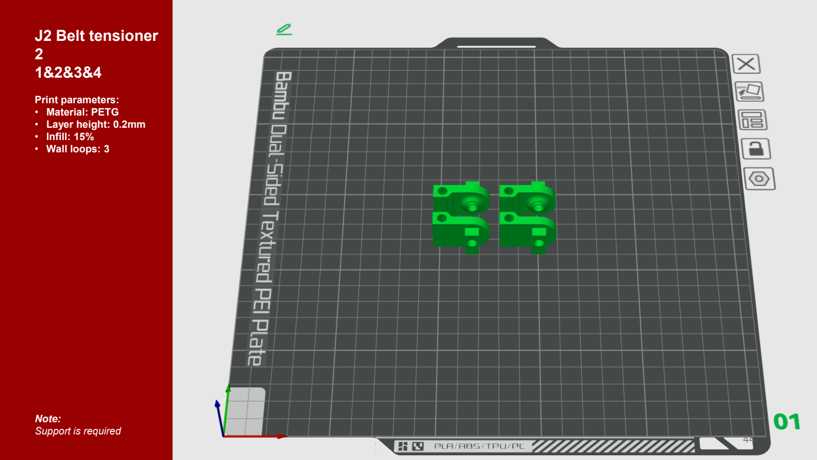
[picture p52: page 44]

Print parameters: • Material: PETG • Layer height: 0.2mm • Infill: 15% • Wall loops: 3

Note:
Support is required

## J2 Belt tensioner 1

1&2

Print parameters: • Material: PETG • Layer height: 0.2mm • Infill: 15% • Wall loops: 3

Note:
Support is required

## BB mount bottom&top

Print parameters: • Material: PETG • Layer height:

0.2mm
- Infill: 15% • Wall loops: 3

## J3 Belt tensioner

1&2

Print parameters: • Material: PETG • Layer height: 0.2mm • Infill: 15% • Wall loops: 3

Note:
Support is required

## Bottom link long

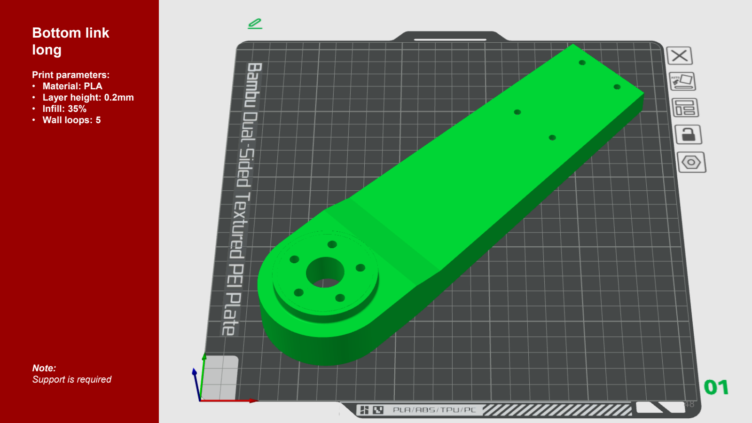
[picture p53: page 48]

Print parameters: • Material: PLA • Layer height: 0.2mm • Infill: 35% • Wall loops: 5

Note:
Support is required

## Bottom link short

Print parameters: • Material: PLA • Layer height: 0.2mm • Infill: 35% • Wall loops: 5

Note:
Support is required

## Gear 20T &

48T

Print parameters: • Material: PETG • Layer height:

0.2mm
- Infill: 100% • Wall loops: 4

## Double gear

100T

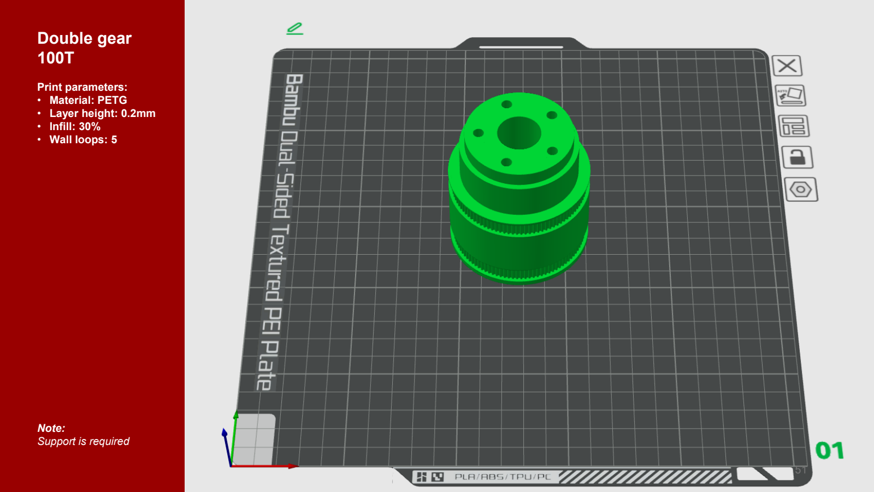
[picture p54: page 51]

Print parameters: • Material: PETG • Layer height: 0.2mm • Infill: 30% • Wall loops: 5

Note:
Support is required

## J3 Cover

Print parameters: • Material: PETG • Layer height:

0.2mm
- Infill: 15% • Wall loops: 2

Note:
Support is required

## J3 Sensor trigger

1&2

Print parameters: • Material: PETG • Layer height: 0.2mm • Infill: 20% • Wall loops: 4

Print the latest verison
instead

## Top link long

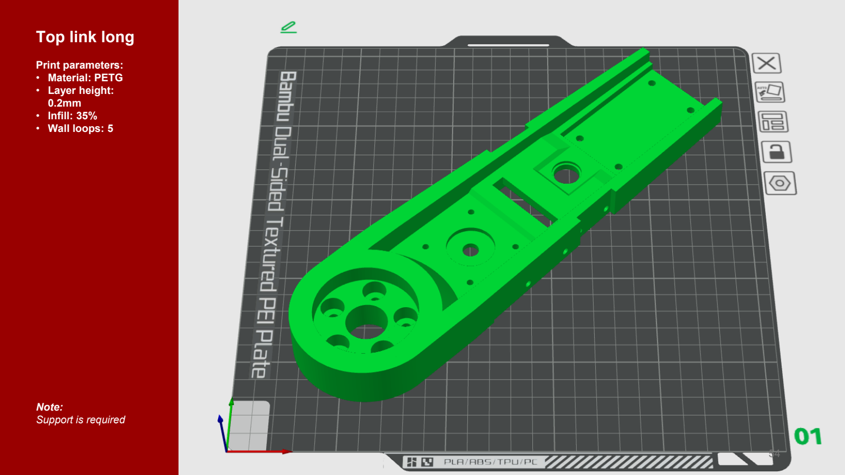
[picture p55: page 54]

Print parameters: • Material: PETG • Layer height:

0.2mm
- Infill: 35% • Wall loops: 5

Note:
Support is required

## Top link short

Print parameters: • Material: PETG • Layer height:

0.2mm
- Infill: 35% • Wall loops: 5

Note:
Support is required

## Gear 80T

Print parameters: • Material: PETG • Layer height:

0.1mm
- Infill: 100% • Wall loops: 4

## Gripper mount

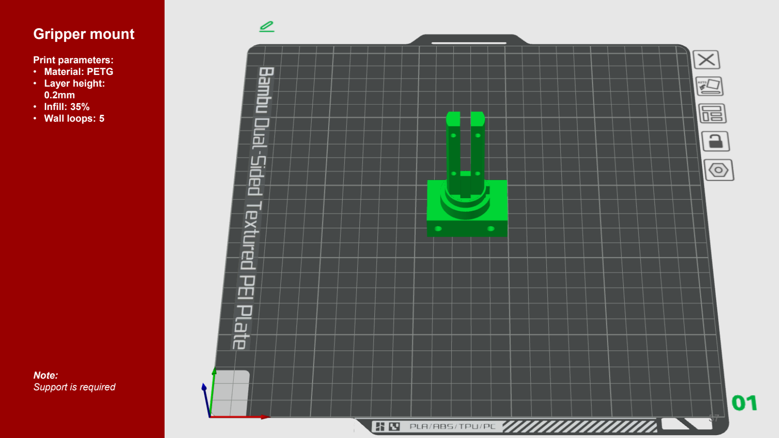
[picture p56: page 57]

Print parameters: • Material: PETG • Layer height:

0.2mm
- Infill: 35% • Wall loops: 5

Note:
Support is required

## J4 Roller

Print parameters: • Material: PETG • Layer height:

0.2mm
- Infill: 15% • Wall loops: 3

Note:
Support is required

## J4 Sensor trigger

Print parameters:
- Material: PETG
- Layer height: 0.2mm
- Infill: 20%
- Wall loops: 4

Print the latest verison
instead

## Gripper base

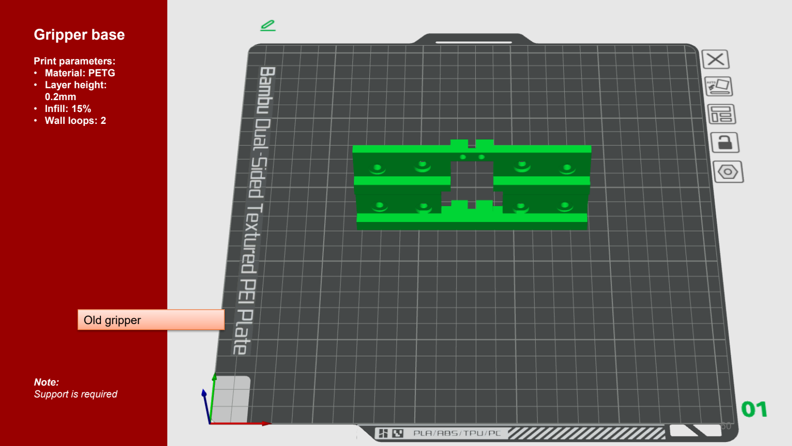
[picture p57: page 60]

Print parameters: • Material: PETG • Layer height:

0.2mm
- Infill: 15% • Wall loops: 2

Note:
Support is required

Old gripper

## Claw mount right & left

Print parameters: • Material: PETG • Layer height:

0.2mm
- Infill: 20% • Wall loops: 4

Note:
Support is required

Old gripper

## Gripper mount left & right

Print parameters: • Material: PETG • Layer height:

0.2mm
- Infill: 15% • Wall loops: 2

Note:
Support is required

Old gripper

## Tube mount left & right

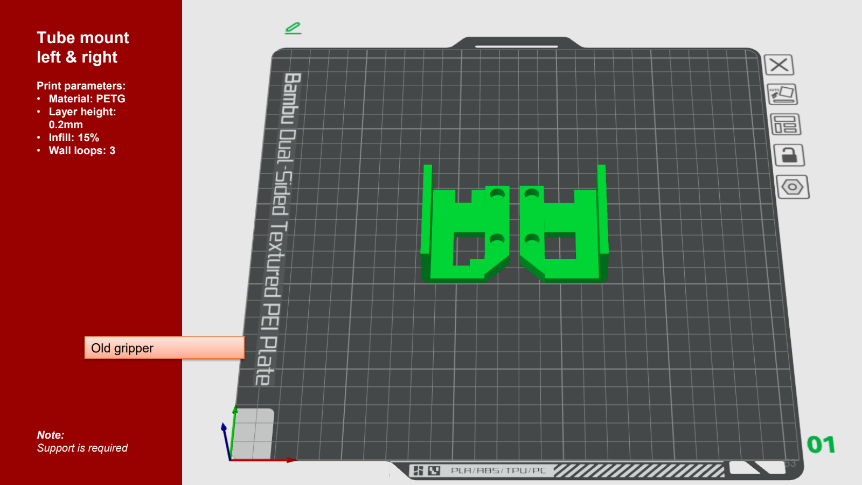
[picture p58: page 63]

Print parameters: • Material: PETG • Layer height:

0.2mm
- Infill: 15% • Wall loops: 3

Note:
Support is required

Old gripper

## Rack gear left & right

Print parameters: • Material: PETG • Layer height:

0.1mm
- Infill: 100% • Wall loops: 4

Old gripper

## Spur gear 16T

Print parameters: • Material: PETG • Layer height:

0.1mm
- Infill: 100% • Wall loops: 4

Old gripper

# JOINTS

Old gripper

# ACTUATORS

## MOTORS

Place the magnet on the motor’s shaft rear end (gluing it is good practice to ensure it will stay put). Try to align the magnet on the shaft as precise as possible. Mount the as described by

## the manufacturer: https://ustepper.com/productsheets/Product_sheet_S32.pdf

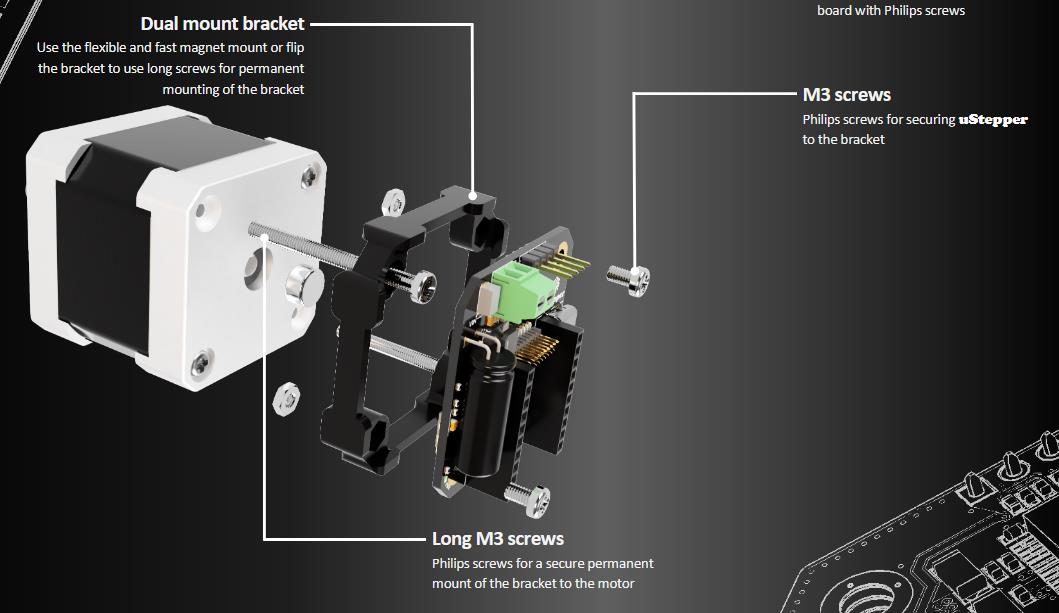
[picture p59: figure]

## WIRING SEQUENCE Connect the motor to the MKS Servo 42C using the JST XH2.54-4Y connector. Refer to the previous page regarding the phase wiring sequence. The motor wiring is an

important step that has to be checked before assembling the whole robot.

The default wiring sequence for the motor used in joint 4 is different than in the other motors. Use the cable provided for

this motor. (assuming the components are identically sourced)

To make sure the wiring is correct, you can measure the resistance between the wires after it has been connected to the motor. In a bipolar stepper motor, the ends of the coil are represented as two pairs – A+ and A- as well as B+ and B-. The measured resistance between the two ends of each pair should be 0 Ω.

An incorrectly wired motor will result in a short when powered. This might be indicated by the motor not being able to move, very high current draw and a buzzing sound.

M

# ENDSTOPS

## ENDSTOPS

Physical Endstops need to be placed to limit the motion and provide a back stop for the sensorless homing.

Joint 1 | Joint 2

## Joint 3

## Joint 4

For Joint 1: place the endstop exactly in the front. Symmetrically counting teeth helps finding the middle.

# ASSEMBLY

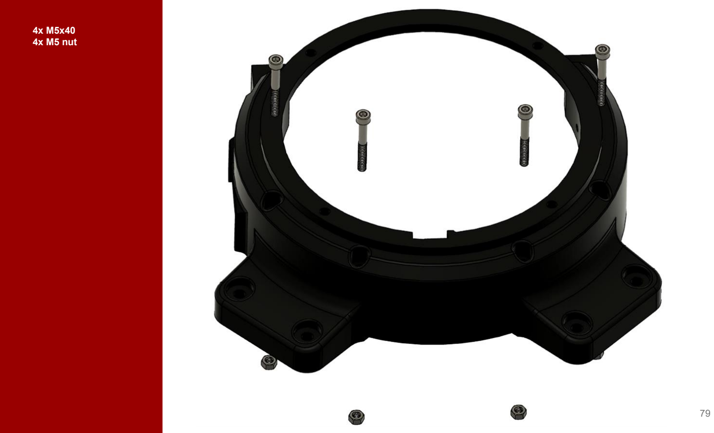
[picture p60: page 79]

4x M5x40
4x M5 nut

2x M4x40
2x M4 nut

Note:
Don’t insert all 4
screws!

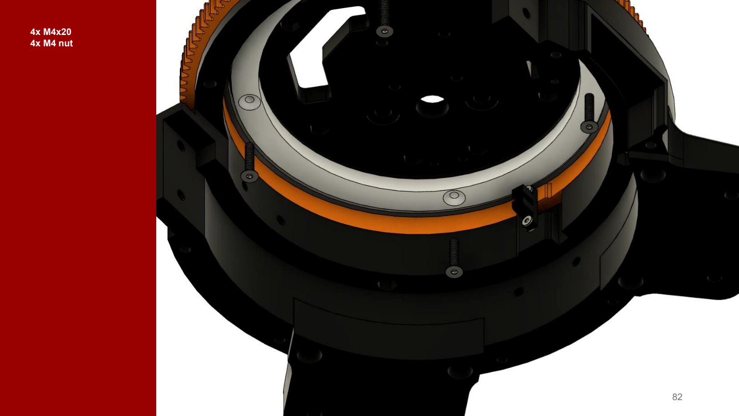
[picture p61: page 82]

4x M4x20
4x M4 nut

2x M5x50
2x M5 nut

2x M5x50
2x M5 nut

2x M4x40
2x M4 nut

4x M5x15

4x M5 nut

Insert power supply into
the PSU box

2x M4x15
2x M4 washer

4x M4x10

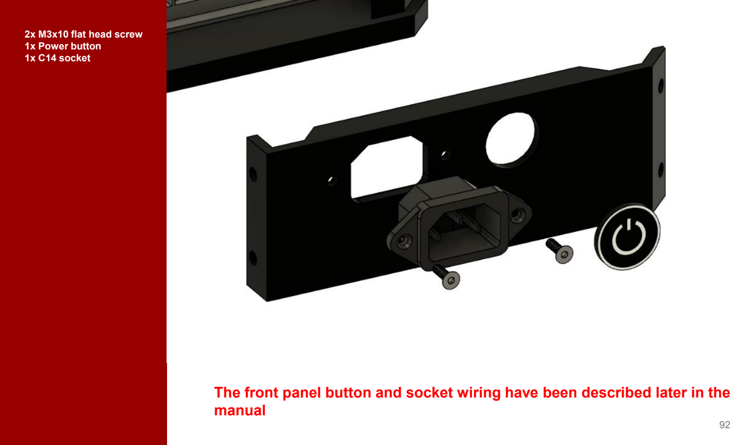
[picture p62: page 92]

2x M3x10 flat head screw
1x Power button
1x C14 socket

## The front panel button and socket wiring have been described later in the manual

4x M4x10

3x M4x8

1x 10mm Pillow ball bearing 10x M5x20
10x M5 nut

2x M5x30
2x M5 nut

6x M5x20
6x M5 nut

1x Ustepper S32
1x Nema 17 (17HS19-2004S1) 1x Planetary Gearbox 5:1
4x Distance washer

4x M3x8
4x M3x10
4x M4x8 flat head screw
1x M3x10

4x M5x20
4x M5 nut

2x M4x10

4x M5x30
2x M4x10
4x M5 nut

2x M5x20
2x M5x10
4x M5x15
8x M5 nut

8x M5x10
8x M5 nut

4x M3x15

3x Steel rod 500x12
1x 4mm Lead screw 500x10

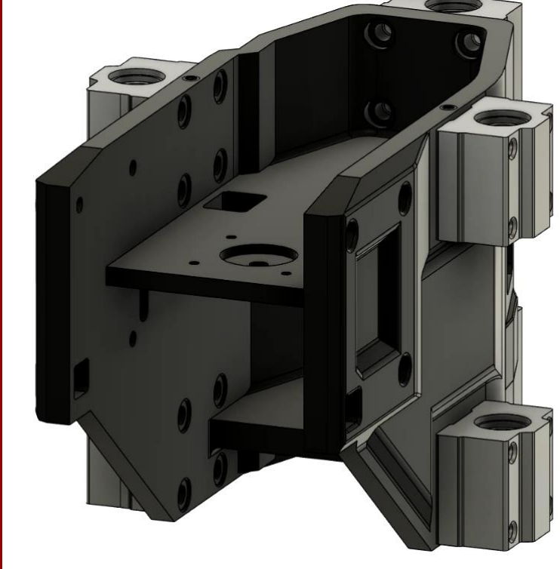
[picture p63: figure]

6x Linear ball bearing block

8x M5x15

8x M5x15

8x
M5x15

1x Lead screw
nut
4x M3x20
4x M3 nut

Slide arm onto rods and
check if lead screw
rotates freely.

1x Shaft coupling 5x10
3x Rod support SHF12

1x Nema 17 (17HS19-2004S1) 1x Ustepper S32

6x M5x15
6x M5 nut
4x M3x10

4x M3x15
4x M3 washer
6x M5x15
6x M5 nut

4x M4x10

1x Nema 17 (17HS15-1504S1) 1x MKS Servo42C
4x M3x10
4x Distance washer

1x GT2 16T Pulley
4x M3x10

6x M5x20
6x M5 nut

1x Ball bearing 50x65x7

2x Ball bearing 5x11x5
4x M3x15
4x M3 nut

1x M5x75
1x GT2 belt 10x294
1x GT2 belt 6x400

Add the belts onto the
3D printed pulley
Position the pulley
inside the arm and insert
the screw
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

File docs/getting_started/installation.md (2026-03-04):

# Installation
This guide describes how to to install and setup all devices to operate the robot. At the first two chapters contain device specific details while the latter can be applied to both the robot controller and a control PC.

:::{important}
This installation guide has not been tested in its entirety. It can thus happen that a prerequisite has been missed, use your own problem solving skills to fill the gap! If you find missing information, include it into this document!
:::

## Robot Controller (Raspberry Pi 4B 4GB) Specific
The following section describes the installation steps specific to the Raspberry Pi robot controller.

### Creating the Boot Image
Using the latest version of the [Raspberry Pi imager](https://www.raspberrypi.com/software/), flash an SD card (16GB, Class 10) with Ubuntu 24.04 LTS Server.
:::{note}
Since the HDMI ports of the Raspberry Pi are no longer accessible when installed inside the robot, follow the next steps to configure remote access.
:::

Flash the SD card with the boot image, you don't need to set custom settings, this will be done in the next step.
**Do not boot the Raspberry Pi yet!**

#### Configuring the Network
When the flashing is finished, copy the *installation/network-config* file to the */boot/* partition of the SD card. 

The *network-config* contains the initial netplan configuration. This file will only be read once per instance (during the first boot). The contents of *network-config* will be copied to */etc/netplan/50-cloud-init.yaml* when installed on the Raspberry Pi [further information](https://docs.cloud-init.io/en/latest/reference/network-config-format-v2.html#netplan-passthrough).

The netplan contains the following configutation:
- Sets the Netplan renderer (the backend for which Netplan is creating the configuration files) to NetworkManager.
- WiFi:
  - Saves an AP with the SSID: "DALSA_IOT" and pre-shared key: "dalsa_iot". See [networking guide](network.md#temporary-wifi-connection) for a description how to use this fallback connection.
- Ethernet:
  - Configures static routing for the "eth0" interface for a LAN. See the network architecture [here](network.md#architecture).
  - The static IP of the robot (the Raspberry Pi) is set to `10.10.10.2`.
  - The ethernet route gets assigned a higher metric to route internet traffic through the WiFi interface if it is connected, since the LAN has not internet access.

#### Troubleshooting

For unknown reasons, while testing theses instructions, it has happened that the Pi was not connecting to the AP nor ethernet. Logging into the Pi with a screen attached showed that the NetworkManager was not installed on the system, this should not happen on a clean installation. If that should happed try one of the following:
- Create a new boot SD card, but edit *network-config* to use 'networkd' (the systemd-networkd network service) instead of 'NetworkManager' as the Netplan renderer. Then, when booted up and connected to a network, install the NetworkManager (`sudo apt install network-manager`). Edit */etc/netplan/50-cloud-init.yaml* back to 'NetworkManager' as renderer and apply `sudo netplan apply`. The network should now be up and managed by the NetworkManager, not systemd-networkd.
- Instead of creating a new boot image, connect to the Pi's shell by attaching display and keyboard and change the renderer to 'networkd', apply `sudo netplan apply`, wait for connection `sudo netplan status -a`, then continue as described above with downloading the NetworkManager.

#### Configuring the User
Copy the *installation/user-data* file to the */boot/* partition of the SD card as well.

The *user-data* file contains mostly configuration for the user *scara* with the password 'dtubio'. The ubuntu cloud-init program manages these configurations during instance deployment. Many settings can be set here, the official README is given for reference:

> *"The user-data of the cloud-init seed. This can be used to customize numerous aspects of the system upon first boot, from the default user, the default password, whether or not SSH permits password authentication, import of SSH keys, the keyboard layout, the system hostname, package installation, creation of arbitrary files, etc. 
> Numerous examples are included (mostly commented) in the default user-data. The format of this file is YAML, and is documented at:<br>
> [https://cloudinit.readthedocs.io/en/latest/topics/modules.html](https://cloudinit.readthedocs.io/en/latest/topics/modules.html) and <br>
> [https://cloudinit.readthedocs.io/en/latest/topics/examples.html](https://cloudinit.readthedocs.io/en/latest/topics/examples.html)"*

You can insert the SD card into the Raspberry Pi and **boot now!** 

Wait for the installation to finish, it will take some time.

### Open Remote Terminal Session
After the installation of the OS has succeeded, we need to log in remotely. The remaining guide assumes you are logged in via ssh to the robot controller.

To do so, first establish a wired or wireless connection to the robot controller as described in the [network guide](network.md) and then log in remotely via ssh:
```bash
ssh scara@<ip-adress>
```

### Connect to the Internet
The following script requires an internet connection. 
Establish an internet connection as described in the [networking guide](network.md#semi-permanent-internet-access-through-dtusecure). 

### Raspi-Config Installation
Installing the Raspi-Config tool on the Ubuntu OS brings some addtional hardware configuation options. 
:::{note}
The exact mechanism and effects of the tool are not fully clear. 
:::

Execute the *installation/scripts/raspi-config_install.sh* script. The source code was provided [here](https://gist.github.com/ryantate13/68882ab4a810369d51da979e37ea9127).

```bash
bash installation/scripts/raspi-config_install.sh
``` 

To apply the changes, restart the robot.

### PWM Activation
In order to use the PWM for servo control, it must be enabled in the */boot/firmware/config.txt* as a "dtoverlay=pwm". However there were issues that the */sys/class/pwm/pwmchip0* could only be used as root. For this reason the *installation/scripts/pwm_activation.sh* registers a udev rule that automatically changes the owner to the "plugdev" group, of which the scara user is a part of. This way the PWM can be controlled without root rights.

```bash
bash installation/scripts/pwm_activation.sh
``` 

### Ensure Low-Latency
To ensure a low-latency operation some settings must be applied. Both of the following settings were already set correctly after the OS installation on the Raspberry Pi. Potentially from the Raspi-config installation(?). Follow the following instructions to ensure they are indeed enabled.

:::{note}
This set of kernel configuration is also set when installing the "Low Latency Ubuntu" (`sudo apt install linux-lowlatency`). But this has not been tested.
:::

#### Preemption Policy 
In mainline Ubuntu the maximum preemption policy is PREEMPT. Ensure the CONFIG_PREEMPT is set:
```bash
cat /boot/<BUILD?> | grep CONFIG_PREEMPT
```
the last known \<BUILD\> was `config-6.8.0-1028-raspi`.

Find more information on the preemption policy [here](https://ubuntu.com/blog/industrial-embedded-systems-ii).

#### Interrupt Timer Resolution
Ensure that a 1000 Hz interrupt timer resolution is set:
```bash
cat /boot/<BUILD?> | grep CONFIG_HZ
```
the last known \<BUILD\> was `config-6.8.0-1028-raspi`.

> *"The timer interrupt handler interrupts the kernel at a rate set by the HZ constant. The frequency affects the timer resolutions as a 100 Hz value for the timer granularity will yield a max resolution of 10ms (1 Hz equating to 1000ms), 250Hz will result in 4ms, and 1000Hz in the best-case resolution of 1ms."* [source](https://ubuntu.com/blog/industrial-embedded-systems-ii)

### Adding the *realtime* Group
Add the user to the realtime group and give it the rights to set higher scheduler priotities as described [here](https://control.ros.org/jazzy/doc/ros2_control/controller_manager/doc/userdoc.html#determinism).

For real-time tasks, a priority range of 0 to 99 is expected, with higher numbers indicating higher priority. By default, users do not have permission to set such high priorities. To give the user such permissions, add a group named realtime and add the user controlling your robot to this group:

```bash
sudo addgroup realtime
sudo usermod -a -G realtime $(whoami)
```
Afterwards, add the following limits to the realtime group in /etc/security/limits.conf:
```
@realtime soft rtprio 99
@realtime soft priority 99
@realtime soft memlock unlimited
@realtime hard rtprio 99
@realtime hard priority 99
@realtime hard memlock unlimited
```
The limits will be applied after you log out and in again.

This **concludes** the robot control specific setup.

## Control PC Specific
The control PC is a desktop PC running the Ubuntu 24.04 LTS Desktop operating system. Its purpose is to be the primary control interface for the user. It is in the same network as the robot controller and thus the ROS2 nodes on the robot controller and control PC can communicate with each other. Recommended use case (at the current development state):
- Run the RViz GUI with the Bioscara Panel, MoveIt and MTC Panel to control the hardware state, manual trajectory generation and sequence inspection
- Since the MTC is not realtime-critical, it can also run on the control PC

### OS Installation
Install the latest Ubuntu 24.04 LTS Desktop release according to [the offical guide](https://ubuntu.com/download/desktop?version=24.04).

Create the following user:
- **User:** *scara-dev*
- **Password:** *dtubio*

All following instructions assume you are logged in to the device.

### Network Configuration
First assign a static IP by creating the */etc/netplan/99_config.yaml* file with following content:
```yaml
network:
  version: 2
  renderer: networkd
  ethernets:
    eno1:
      addresses:
        - 10.10.10.3/24
      routes:
        - to: default
          via: 10.10.10.1
          metric: 700 # Increase the metric so that a the wifi connection (metric: 600) is preffered for internet traffic
      nameservers:
          addresses:
            - 8.8.8.8
            - 8.8.4.4
```
And the following a simple WPA wifi access point:
```yaml
...
  wifis:
    wlp0s20f3:
      dhcp4: true
      optional: true
      access-points:
        "DALSA_IOT":
          password: "dalsa_iot"
...
```

Then add a static hostname entry by adding the following line in the */etc/hosts* file:
```
10.10.10.3 scara-dev
```

Reboot the machine to apply all changes. Changes to the netplan manager can be applied like this:
```bash
sudo netplan apply
```

### Connect to the Internet
Establish an internet connection as described in the [networking guide](network.md#semi-permanent-internet-access-through-dtusecure). 

## Install I2C dependecies
In order to later compile the ROS2 workspace the only external dependency *lgpio* must be installed. 

Execute the *installation/scripts/i2c_libraryAndTools_install.sh* script:
```bash
bash installation/scripts/i2c_libraryAndTools_install.sh
```

## Install ROS2
Use the *installation/scripts/ROS2-Jazzy_install.sh* to install ROS2. The installation requires root priviliges, enter the password when prompted:

```bash
bash installation/scripts/ROS2-Jazzy_install.sh
```

## Clone the Project Repository
Clone the project repository from Github into the *~/bioscara/* repository:
```bash
git clone https://github.com/DALSA-Lab/bioscara.git
```
## Import further Dependecies
Next we are going to install a lot of dependencies, either as a binary or from source.

### Dependecy Management Tools
The order of managing dependenices is according to [this](https://ros2-quality-assurance.readthedocs.io/en/released/tutorials/dependencies.html) guideline the following:
1. **rosdep**: Installs missing binary dependecies specified in the packages via the systems package manager.
2. **vcstool**: Specify further source code repositoryies in a repository file, `vcstool` will then retrieve the repository and it can then be built with colcon. 
3. **other**: Manually install dependecies. (Already finished after install of *lgpio*)

### Clone further Source Code Repositories
This step pulls all dependecies that are not available as binaries.

Navigate to the ROS2 workspace *lib/ros2_ws*:
```bash
cd lib/ros2_ws
```

`vcstool` is found in many ROS2 packages to import dependencies that are not in a ROS or debian repository from a repository file. It should be automatically installed with the ROS2 install script. If not, its binary name is `python3-vcstool`.

Then invoke the `vcstool` to import the repositories specified in the *lib/ros2_ws/req.repos* file:
```bash
vcs import --recursive src < req.repos
```

This will pull the following repositories:
- [***single_trigger_controller***](https://github.com/DALSA-Lab/ros2_control-single_trigger_controller.git) branch: *main*
  - This repository hosted on the DALSA Github contains the SingleTriggerController used to trigger homing. Since the controller is generic, it is hosted as a seperate repository.
- [***moveit_task_constructor***](https://github.com/moveit/moveit_task_constructor.git) branch: *ros2*
  - The MTC is not available as a binary and must thus be built from source.

:::{important}
The following repositories only need to included if the latest available binary MoveIt2 version is < 2.12.4! All newer version will include a bugfix that was not yet released at the time of writing the tutorial.
**TO-DO:** Remove the following repositories from the *req.repos* file if the binary is available.
:::
- [***moveit2***](https://github.com/DALSA-Lab/moveit2-dalsa.git) branch: *main*
  - MoveIt2 is cloned from a DALSA Fork. Using a fork, we have full control over the versioning and it also includes the changes to the Pilz Motion Controller that allow it to be used with any planning pipeline.
- [***moveit_visual_tools***](https://github.com/moveit/moveit_visual_tools.git) branch: *ros2*
  - Only cloned from source due to installation conflicts with the binary
- [***pick_ik***](https://github.com/PickNikRobotics/pick_ik.git) branch: *main*
  - Only cloned from source due to installation conflicts with the binary

### Install even more Repositories
:::{important}
Do this step ONLY if MoveIt is installed from source! This is NOT necessary if it can be installed as a binary.
:::

Recursively import MoveIt's source code dependencies:
```bash
cd src
for repo in moveit2/moveit2.repos $(f="moveit2/moveit2_$ROS_DISTRO.repos"; test -r $f && echo $f); do vcs import < "$repo"; done
```

### Binary Dependencies
This steps installs all packages that can be resolved through `rosdep` (all packages that have been released to the ROS2 package ecosystem and some debian packages):
```bash
cd lib/ros2_ws
sudo apt update
rosdep update
rosdep install -r --from-paths src --ignore-src --rosdistro $ROS_DISTRO -y 
```
This command will recursively scan every package in the workspace for the `<depend/>` key and install missing packages.

As a last step, remove any conflicting MoveIt binaries. This should not be neccessary on a fresh install.
```bash
sudo apt remove ros-$ROS_DISTRO-moveit*
```

### Build the Workspace!
Follow the [building instructions](building.md) to finally compile the entire workspace!

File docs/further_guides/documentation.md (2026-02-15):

# Building the Documentation locally
The documentation consists of two independent parts. The Doxygen-based C++ API documentation and these Sphinx user guides.

## First Steps
All following commands are executed from the *~/bioscara/docs/* directory:
```bash
cd docs
```
## Create the Virtual Environment and Install Dependencies
It is recommended to use a virtual environment to manage all dependencies.
These steps need to be executed only once at the first time.
Create the virtual python environment:
```bash
python -m venv .venv
```

Before installing the dependencies the environment needs to be activated:
```bash
source .venv/bin/activate
```

The we can install the required packages to build the documentation:
```bash
pip install -r requirements-docs.txt
```
This installs Sphinx and its packages.

Aditionally install doxygen
```bash
sudo apt-get update
sudo apt-get install doxygen
```

And install all LaTeX tools:
```bash
sudo apt-get install texlive texlive-font-utils texlive-fonts-recommended texlive-latex-extra latexmk
```

## Building the Documentation

First make sure the virtual environment is activated:
```bash
source .venv/bin/activate
```

Then run doxygen from the *docs/doxygen/* directory to produce HTML, XML and LaTeX output:
```bash
cd doxygen
doxygen
```

Compile the LaTeX to a PDF:
```bash
cd doxygen/latex
make
```

First compile it as a PDF (the HTML will link to it later)
```bash
sphinx-build -M latexpdf . sphinx/latex
```

Finally build the Sphinx documentation:
```bash
sphinx-build -b html . sphinx/html
```

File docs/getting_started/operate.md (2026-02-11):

# Operate the Robot
This document explains how to bring the robot into operation for manual and programmatic control.
The document will decribe how to start the robot hardware as well as its emulation.

## Prerequisites
Make sure that following prerequisites are fullfilled:
- In order for the robot to operate, all software and system configurations must be installed as described in the [installation](installation.md) guide. 
- The ROS2 workspace must be compiled as described in the [build](building.md) guide.
- **For hardware operation:** The robot must be correctly assembled and all components are electrically connected. The latest hardware information can be found [here](../hardware/index.rst)
- A stable wired network connection between the control PC/developers PC and the robot controller is established as described in the [networking tutorial](../getting_started/network.md).

## Connect to the Robot Controller
After a connection has been established to the robot controller, open a ssh session from the control PC:
```bash
ssh scara@<ip-adress>
```
Type the password **dtubio** when prompted and hit enter. You should now have a terminal session on the robot controller and you can proceed.

## Starting the Robot

:::{warning}
You are about to enable the robot! Make sure it is securely mounted and its workspace is clear!
:::

Change to the *lib/ros2_ws* directory:
```bash
cd lib/ros2_ws
```
All following commands are relative to this directory.

Source the workspace packages:
```bash
source install/local_setup.bash
```

### Launch the robot control nodes
To start all ROS2 nodes simultaneously launch the complete launch file:
```bash
ros2 launch bioscara_arm_gripper_128_moveit_config complete.launch.py
```
This will start the ros2_control node responsible for the control implementation and the MoveIt2 move_group node for trajectory generation.

:::{note}
With no access to the hardware it is possible to emulate it by passing the `use_mock_hardware:=true` argument to the launch file:
```bash
ros2 launch bioscara_arm_gripper_128_moveit_config complete.launch.py use_mock_hardware:=true
```
:::

### Launch the RViz GUI
The RViz GUI is needed for vsizualization and to control the Bioscara hardware, to example home it.
Since the robot controller does not have a desktop, the control GUI must either run on a seperate control PC or must be forwared via ssh. In both cases a stable and fast network connection is critical to ensure timely updates.

#### Using Window Forwarding
This method has the advantage that the external control PC does not need have ROS2 installed. A ssh client capable of X-forwarding is sufficient.

Open a second ssh session from the control PC to the robot controller with X-forwarding enabled:
```bash
ssh scara@<ip-adress> -X
```

Start the RViz GUI on the robot controller, it will be forwarded to the control PC:
```bash
ros2 launch bioscara_arm_gripper_128_moveit_config moveit_rviz.launch.py
```

#### Using an Networked PC with ROS2 installed
Using this method requires the control PC to have ROS2 installed, along with RViz2, the Bioscara RViz plugin, the MoveIt Panel and MTC Panel. The advantage is that the robot controller has less computation load, since it does not need to display the RViz process.

In this case it is sufficient to simply open a new local terminal session.
Start the RViz GUI on the robot controller:
```bash
ros2 launch bioscara_arm_gripper_128_moveit_config moveit_rviz.launch.py
```

### Alternative: Manually launching Nodes
If you experience problems with the complete launch file or to try differnent launch configurations, you can try to launch the components indiviudally.
First launch the ros2_control node with the *scene_bringup* packages:
```bash
ros2 launch scene_bringup bioscara_arm_gripper128.launch.py use_mock_hardware:=true/false
```

Then launch the move_group seperately:
```bash
ros2 launch bioscara_arm_gripper_128_moveit_config move_group.launch.py
```

## Preparing the Robot
You should now see the RViz GUI like this

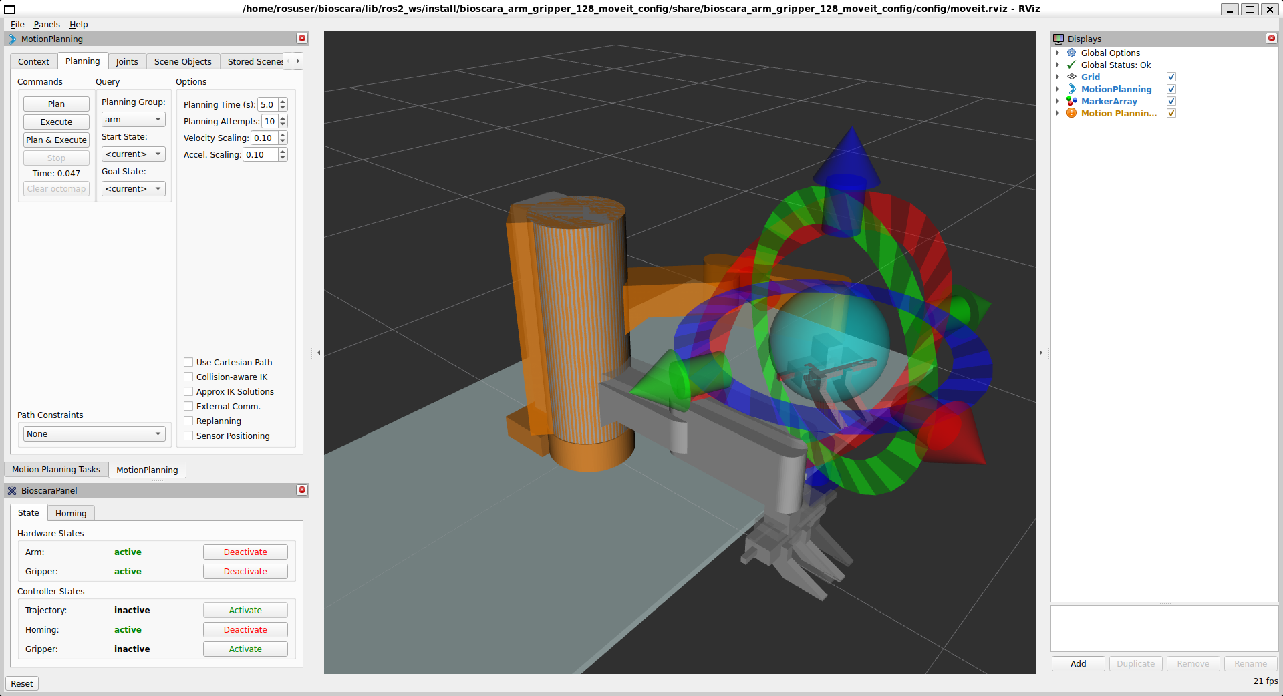
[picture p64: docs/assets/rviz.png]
Rviz GUI


The important panel are on the left side. On the top left you can find the MoveIt *MotionPlanning* and MoveIt-Task-Constructor *Motion Plannining Tasks* Panel. But before we get to that the robot has to be configured for operation with the bottom left *Bioscara* Panel.

### Homing the Robot
If the robot has been power-cycled, its joint's need to be homed again. To do this activate the homing controller under the "State" tab as displayed in the picture above. The navigate to the "Homing" tab where you should see all joints as "Not Homed". During homing the joint will slowly drive towards its upper or lower limit where it will detect the collission and zero its encoder. You can select the direction through the buttons right of the joint label as it suits you best. Make sure that the joint can move freely and that it actually stops at its endstop. Repeat this until all joints report "Ready" as shown in the picture below:

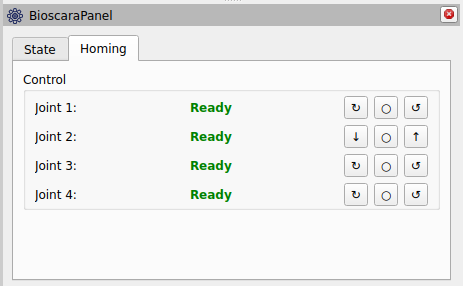
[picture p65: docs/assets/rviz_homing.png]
Rviz homing


### Enabling the Controllers
Now with the robot homed it is almost ready for operation. Under the "State" tab, deactivate the homing controller then activate the trajectory and gripper controller. The arm and gripper hardware must also be active. All joint motors are now engaged and can not be backdriven. To backdrive the robot deactivate the Arm hardware.

## Manually Create Trajectories
It is possible to manually plan trajectories, execute them, compare path planner performance and more with the *MotionPlanning* panel.
The [official tutorial](https://moveit.picknik.ai/main/doc/tutorials/quickstart_in_rviz/quickstart_in_rviz_tutorial.html) gives a good introduction hot to use it.

In short: Use the handles to move the orange goal robot state into a desired pose, then press "plan" and/or "execute" under the "Planning" tab. By default the OMPL RRTConnect path planner is used to plan the paths, alternatives can be selected under the "Context" tab.

### Planning Scene
Under the "Scene Objects" tab the planning scene can be modified. Collision objects can be added, modified and removed from it, or a a setup can be imported. Always press "publish" to commit the changes to the planning scene.

## Planning and Executing a MTC Task
The MoveIt-Task-Constructor (MTC) is used to plan more complex trajectory sequences. The tasks are created in the *dalsa_motion_plans* package. Python scripts are the easiest to edit and create, although it seems that not all C++ methods are fully supported through the Python bindings. The Python scripts are in the *dalsa_motion_plans/scripts* directory.

The MTC can be run either on the robot contoller or the control PC since it is not realtime-critical. Exectute the following steps on the robot controller or control PC respectively.

### Adding a new MTC Task
A sort-of correct documentation for the Python bindings can be found [here](https://moveit.github.io/moveit_task_constructor/).
Using these recipes complex applications can be programmed. Some examples can be found in the */scripts* dir, have fun!

To create a new Python script with a new MTC task the following needs to be done:
- Create the *cool_task.py* under *dalsa_motion_plans/scripts*
- Add the script to the *dalsa_motion_plans/CMakeLists.txt*. Find the following lines and append the the *cool_task.py* to the list of installed files.
```cmake
install(PROGRAMS
        scripts/IAmNotARobot.py
        scripts/PickPlace.py
        scripts/PickPlace_continous.py
        scripts/PickPlace_markers.py
        scripts/cool_task.py                # <===== Append here
        DESTINATION lib/${PROJECT_NAME})
```
- In order to make the script available rebuild the *dalsa_motion_plans* package:
```bash
colcon build --symlink-install --mixin release --packages-select dalsa_motion_plans
```

### Executing the Task
From a new terminal, navigate to the *lib/ros2_ws* worspace and source it `source install/local_setup.bash`. Then you can execute any MTC task by invoking
```bash
ros2 launch dalsa_motion_plans run.launch.py exe:=cool_task.py
```
where the `exe` argument specifies the name of the script to execute.

If the task planned succesfully, it is published to the "/solution" topic and displayed in the *Motion Planning Tasks* MTC Panel shown below. For each task a number of solutions can be computed which can be indivdually inspected and, if one is selected, executed by pressing the Exec button.

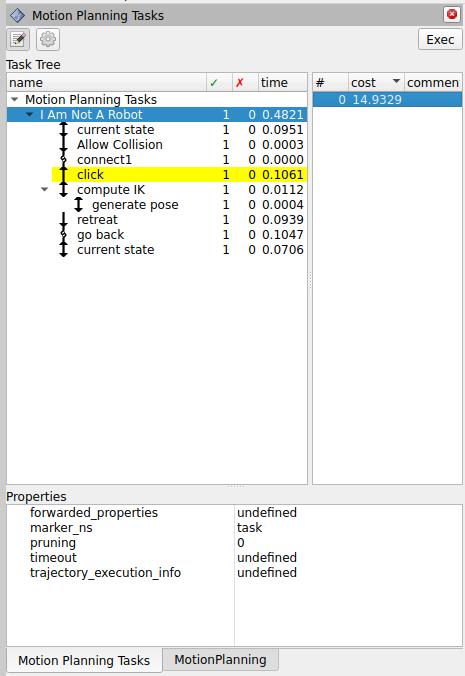
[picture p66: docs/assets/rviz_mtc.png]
Rviz mtc


## Common Problems
Some common issues and remedies are described in the following.

### General Launch Problems
If nodes fail to launch and no clear error message is printed in the console try one or a combination of the following:
- Open a new terminal and source the workspace again
- Build the workspace or the affected packages again and execute the above step.
- Remove the affected packages from the *lib/ros2_ws/install/\<package\>* and *lib/ros2_ws/build/\<package\>* directory and execute the above steps.

### Motion Planning Fails
This can have many reasons, the exact move_group error usually helps to identify the issue.
- **Start state out ouf bounds:** If a joint is just a tenth of a millimeter outside its limit, motion planning will fail. If the gripper is causing the violation, manually send a new width command through the console `ros2 action send_goal /gripper_controller/gripper_cmd control_msgs/action/ParallelGripperCommand "{command:{name:[gripper],position:[0.05]}}"`. If the problematic joint is on the robot arm and not J2, just deactivate the robot arm, move the joint away from the limit and reactivate the arm again. If the problematic joint is J2 it can not be moved by hand. Instead do the following: Open another terminal navigate to *lib/ros2_ws/*, source the workspace, and start the rqt_joint_trajectory_controller: `ros2 run rqt_joint_trajectory_controller rqt_joint_trajectory_controller`. Select the "controller_manager" and "velocity_joint_trajectory_controller", enable it on the red button and manually drag the J2 set point away from the limit. This GUI can also be used for other purposes but it should never be active in parallel with an ongoing trajectory through MoveIt.

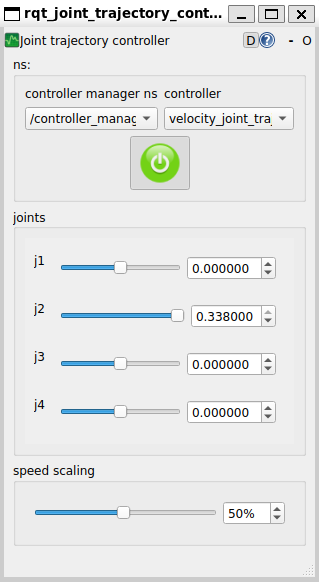
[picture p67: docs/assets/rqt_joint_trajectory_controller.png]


- **Start state collision:** If a trajectory is planner immediatly after homing , the gripper links can be in a self-collision with link link_1, since the collision body is a primitive cylinder. Simply deactivate the arm and move the links out of collision. The collided links will be highlighted in red in RViz.

### ros2_control Fails to Start
Sometimes, for yet unknown reasons, if the ros2_control node is launched from the complete launch file, it attempts to start the robot hardware despite the `use_mock_hardware:=true` has been set.
If that happens while no hardware is connected, the node will fail to start and control is impossible. Launching the ros2_control node separately as described in [here](#alternative-manually-launching-nodes) seems to resolve this issue.

### Homing Sequence not Starting/Finishing
As described in [this bug](https://github.com/DALSA-Lab/bioscara/issues/5) report, under yet unclear conditions, the homing sequence is immediatly aborted after it has been started. The joint driver however assumes it is sill ongoing while the firmware has already finished it. This issues can be fixed by:
1) Stop the homing sequence by pressing the `o` button
2) Restart homing

<!-- TODO: where to modify dynamic limits -->

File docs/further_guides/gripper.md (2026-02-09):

# Standalone Gripper Operation
This document describes the simplest way to manually control the gripper. This is desireable for development and necessary after assembly to recalibrate the grippers reduction and offset. The current gripper is driven by a PWM controlled RC servo. The frequency is 50 Hz. The PWM should be a hardware generated PWM as software PWM has potentially high jitter which could cause overheating. The gripper is controlled through its C++ API defined in the *bioscara_gripper_hardware_driver::Gripper* object.

## Connect to the Robot Controller
Follow the [networking tutorial](../getting_started/network.md) to establish a connection to the robot controller. When a connection has been established login to the controller via ssh:
```bash
ssh scara@<ip-adress>
```
Type the password **dtubio** when prompted and hit enter. You should now have a terminal session on the robot controller.

## Manual Operation
The gripper can be manually controller by executing the `gripper_manual_control` program. First, ensure that the entire workspace is built by following the [build](../getting_started/building.md) instructions. At a minimum, the `gripper_manual_control` and `bioscara_gripper_hardware_driver` packages must be built. You can manually build them by executing:
```bash
cd lib/ros2_ws/
colcon build --symlink-install --packages-select gripper_manual_control bioscara_gripper_hardware_driver
```

This system test package contains a simple programm that allows to manually control the gripper actuator. The program can be used in two ways:
1) Setting the desired width. This can only be used when the correct reduction and offset is known. **If they are unkown**, use the 2) mode and follow the steps described there.
2) Setting the servo angle directly. This should be used for testing, positioning when mounting and dismounting and to calculate reduction and offset (explained [here](#calculating-reduction-and-offset)).

### Running the program
Open a new terminal session on the robot controller, navigate to the *lib/ros2_ws/* directory and source it.
```bash
cd lib/ros2_ws/
source install/local_setup.sh
```
:::{tip}
Sourcing the executables is only is necessary once after opening a new terminal.
:::

You can then run the executable:
```bash
ros2 run gripper_manual_control manual_control
```
Now follow the instructions given in the console output.

## Calculating reduction and offset
The gripper has the reduction $r$ and offset $o$ parameters which are used to translate from a desired gripper width to the servo angle. These paramters must be supplied to the gripper hardware interface when used for normal operation. 

:::{warning}
The gripper will be damaged, if the reduction and offset paramters are incorrect. The parameters must always be calibrated after dissassembly and on initial commissioning.
:::

The relationship between gripper width $w$ and acutator angle $\alpha$ is as follows:
$$
\alpha = r (w-o)
$$

To determine these parameters execute the following steps:

1. Manually set the gripper to an open position by setting an actuator angle. Be careful to not exceed the physical limits of the gripper since the actuator is strong enough to break PLA before stalling.
2. Measure the gripper width between the jaws $w_1$ and note the commanded actuator angle $\alpha_1$.
3. Move the gripper to a more closed position that still allows you to accurately measure the width.
4. Measure the second width $w_2$ and note the corresponding angle $\alpha_2$.
5. Calculate the offset $o$:

$$
o = \frac{\alpha_1 w_2 -  \alpha_2 w_1}{\alpha_1 - \alpha_2}
$$

6. Calculate the reduction $r$:

$$
r = \frac{\alpha_1}{w_1 - o}
$$

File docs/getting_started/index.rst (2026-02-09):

Getting Started
===============

.. toctree::
   :maxdepth: 2
   :caption: Contents

   installation.md
   building.md
   operate.md
   network.md

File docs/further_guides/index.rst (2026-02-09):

Developer Guides
================

.. toctree::
   :maxdepth: 2
   :caption: Contents

   gripper.md
   firmware.md
   documentation.md   
   IKFast.md

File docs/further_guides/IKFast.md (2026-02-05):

# Creating a IKFast Inverse Kinematics Plugin
:::{important}
This guide can only serve as a starting point since the desired result could not be achieved!
:::

The IKFast is an analytical inverse kinematics solver that automatically generates a robots IK solver code based on its URDF file. This guide documents which steps have been undertaken to generate the IKFast solver plugin for MoveIt. 

The result however has always been that the robot did not move when dragging on its handles in MoveIt.

## Background
Please refer to the original guide on the MoveIt documentation page [here](https://moveit.picknik.ai/main/doc/examples/ikfast/ikfast_tutorial.html) for the information about the individual commands.

## Plugin Creation

make sure Docker is installed: 
```bash
docker -v
```

If that is not the case install Docker by following the guide [here](https://docs.docker.com/engine/install/ubuntu/).

if that is done, make sure your user is added to the "docker" group:
```bash
sudo usermod -aG docker ${USER}
```

log out and back in to apply the new group:
```bash
su -l ${USER}
```

navigate to the *lib/ros2_ws/src/dalsa_bioscara_arm* directory:
```bash
cd lib/ros2_ws/src/dalsa_bioscara_arm
```

export the arm as an ENV variable:
```bash
export MYROBOT_NAME="bioscara_arm"
```

Create a urdf file from the *scene.xacro* which will be parsed by the plugin generation script.
```bash
ros2 run xacro xacro -o $MYROBOT_NAME.urdf bioscara_arm_description/urdf/scene.xacro
```

Then create then call the plugin creation script:
```bash
ros2 run moveit_kinematics auto_create_ikfast_moveit_plugin.sh --iktype <type> $MYROBOT_NAME.urdf arm base_link tool_flange
```
On first run this will take a while to pull and build the docker images.

Select one 4-DOF \<type\> from the following ([source](https://openrave.org/docs/latest_stable/openravepy/ikfast/#ik-types)):

- **Transform6D** - end effector reaches desired 6D transformation
- **Rotation3D** - end effector reaches desired 3D rotation
- **Translation3D** - end effector origin reaches desired 3D translation
- **Direction3D** - direction on end effector coordinate system reaches desired direction
- **Ray4D** - ray on end effector coordinate system reaches desired global ray
- **Lookat3D** - direction on end effector coordinate system points to desired 3D position
- **TranslationDirection5D** - end effector origin and direction reaches desired 3D translation and direction. Can be thought of as Ray IK where the origin of the ray must coincide.
- **TranslationXY2D** - end effector origin reaches desired XY translation position, Z is ignored. The coordinate system with relative to the base link.
- **TranslationLocalGlobal6D** - local point on end effector origin reaches desired 3D global point. Because both local point and global point can be specified, there are 6 values.
- **TranslationXAxisAngle4D**, **TranslationYAxisAngle4D**, **TranslationZAxisAngle4D** - end effector origin reaches desired 3D translation, manipulator direction makes a specific angle with x/y/z-axis (defined in the manipulator base link’s coordinate system)
- **TranslationXAxisAngleZNorm4D**, **TranslationYAxisAngleXNorm4D**, **TranslationZAxisAngleYNorm4D** - end effector origin reaches desired 3D translation, manipulator direction needs to be orthogonal to z, x, or y axis and be rotated at a certain angle starting from the x, y, or z axis (defined in the manipulator base link’s coordinate system)

None of the last 6 types have yielded a successfull result yet.

## Build the new Plugin Package
Navigate to the root of the workspace:

```bash
cd lib/ros2_ws
```

and build the new package:
```bash
colcon build --symlink-install --mixin release --packages-select bioscara_arm_ikfast_plugin
```

## Change the kinematics.yaml
Almost done, change the *lib/ros2_ws/src/moveit_configurations/bioscara_arm_gripper_128_moveit_config/config/kinematics.yaml* file to the new IK solver:
```yaml
arm:
  kinematics_solver: bioscara_arm/IKFastKinematicsPlugin
  ...
```

## Try it out
Start the robot (mock or hardware), move_group and rviz as described in the [guide](../getting_started/operate.md).

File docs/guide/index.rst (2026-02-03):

User Guides
=============

.. toctree::
   :maxdepth: 3
   :caption: Contents

   installation.md
   building.md
   operate.md
   documentation.md   
   firmware.md
   IKFast.md

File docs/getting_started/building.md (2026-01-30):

# Building the ROS2 Workspace
After importing all dependencies the ROS2 workspace *lib/ros2_ws/* will contain a lot of packages, primarily MoveIt and MTC packages along the usual Bioscara packages.
In order to be able to run them, they all have to be built. `colcon` is the ROS2 building tool that is used for this purpose.

:::{note}
 This guide assumes that you are in the *lib/ros2_ws/* workspace.
 If you are not, navigate to it:
 ```bash
    cd lib/ros2_ws/
 ```
:::

## Building the Entire Workspace including MoveIt2 and MTC
Both MoveIt2 and the MTC are huge packages that will make the Raspberry Pi crash under the load. Even for normal computers there is a high chance of freezing.
For this reason the `colcon build` command is invoked with very restrictive parameters to allow the compilation to finish at all.
The build command that should be used to compile the entire workspace at once is:
```bash
MAKEFLAGS="-j1 -l1" colcon build --mixin release --executor sequential --symlink-install --continue-on-error > log.out &
```
```bash
disown
```
The `MAKEFLAGS="-j1 -l1"` restrict the process to a single core, the `--executor sequential` flag ensurs that only one package at the time is built (otherwise up to 8 would be built), the `--continue-on-error` flag will try to keep the compilation going if one package fails. This is very important since the compilation can take up to 10 (!) hours on the Raspberry Pi 4B with 4GB memory. 

The high memory usage will cause the Raspberry Pi to become unresponsive at times, potentially dropping the SSH connection and thus the user session that started the build proces. 
To avoid this the `colcon` output is being piped `> log.out` to a file and the process is being sent to the background `&`. Before disconnecting from the session the process must be disowned by calling `disown`. The build job will now continue even if the user session that started it terminates. 

## Building selected Packages
Luckil as long as you dont modify any of the MoveIt or MTC packages or accidentally delete the *build/* or *install/* directories, you will not have to build the entire workspace again.
To rebuild a selected set of packages simply invoke `colcon` like this:
```bash
colcon build --mixin release --symlink-install --packages-select <package_name> <package_name> <package_name>
```
or select the by a regex expression `--packages-select-regex <package_name_regex>` or any other (selection flag)[https://colcon.readthedocs.io/en/released/reference/package-selection-arguments.html]

## Other Notes
Using the `--symlink-install` flag create symlinks instead of copying files from the source and build directories where possible. This way it is not necessary to recompile a package if a non-C++ file has been modified. Changing parameter yaml-files, Pthyon scripts or URDF files is thus simpler and faster. 

The `--mixin release` makes the packages compile in release mode, which is very important for performance reasons. Not using this flag will make path planning very slow.

If compilation fails, in particular if a package's *CMakeLists.txt* has been modified, it can help to selectively clean the *build/* and *install/* directory:
```bash
rm -rf build/<package_name> install/<package_name>
```

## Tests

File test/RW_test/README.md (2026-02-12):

# Communication Read/Write speed test
The realtime performance tests described in the [realtime test](../RT_test/README.md) showed slow execution times for both the read and write cycle. To be precise the test measured the following average cumulative execution times for all joints:
- **Read** (*getPosition*): 3465 μs
- **Write** (*setPosition*): 4964 μs

> [!NOTE]
>
> When conducting the realtime test the position joint trajectory controller was used. In the latest iteration the velocity joint trajectory controller is used. 

This test is to identify the bottleneck that causes the long execution times and to investigate if they can be increase to enable higher controller update rates.

## Description
The test consists of two units:
### Joint Firmware
A firmware variant ([profiling_test.ino](../../lib/joint_firmware/profiling_test/profiling_test.ino)) is flashed on the joint controller. This firmware times the execution of the `non_blocking_handler()` which handles the incoming commands and prints the results to the serial port in CSV format. The development machine stays connected to the joint via USB to capture the serial port output and save it to a file. The [Realterm](https://sourceforge.net/projects/realterm/) software was used to cpature and save the serial output. 
### Controller
The controller executes the system_test_packages/comm_speed_test program
```bash
cd lib/ros2_ws
source install/local_setup.bash
ros2 run comm_speed_test main
```
The test program calls and times the read and write execution duration of either position or velocity (`getPosition()`/`getVelocity/()` and `setPosition()`/`setVelocity/()` respectively) for a total of 1000x cycles per joint and prints the collected data to a CSV file.

No prints and other unneccessary functions are executed in the timed sections.

## Background
### I2C Protocol
The robot controller and joints communicat via an I2C bus. [This](https://www.ti.com/lit/an/slva704/slva704.pdf) document describes the protocol in detail, below the transmitted bytes are summarized in Table 1 below. Counting the number of transmitted bits is important since the I2C bus clock runs at a speed of 100 kHz (100 kbit/s) or 400 kHz (400 kbit/s).

|Sender|      |         |       |      |        |      |        |      |      |        |      |      |         |       |      |        |      |      |        |       | | Bits                 |
| ---- | ---- | ------- | ----- | ---- | ------ | ---- | ------ | ---- | ---- | ------ | ---- | ---- | ------- | ----- | ---- | ------ | ---- | ---- | ------ | ----- | ---- | ---------------- |
|*Controller* | S[1] | Addr[7] | Re[1] |      | Reg[8] |      | TX*1*[8] |      | ...  | TX*m*[8] |      | S[1] | Addr[7] | Re[1] |      |        | A[1] | ...  |        | NA[1] | P[1] | 27+*n*+8\**m*       |
|*Target* |     |         |       | A[1] |        | A[1] |        | A[1] | ...  |        | A[1] |      |         |       | A[1] | RX*1*[8] |      | ...  | RX*n*[8] |       |      | 3+8\**n*+*m*       |
|      |     |         |       |      |        |      |        |      |      |        |      |      |         |       |      |        |      |      |        |       |      | **30+9\**n*+9\**m*** |

**Table 1:** I2C transmission frames for a combined Read/Write. The number in [n] brackets are the number *n* of transmitted bits in this frame.

> [!NOTE]
>
> The sum of bits in Table 1 is only true for combined Read/Write transmission. In this application every transmission is a Read/Write transmission since at a minimum the return flags are always read from the joint. For a single write transmission with *m* transmitted bytes, the total number of transmitted bits is slightly different (repeated start and repeated address are ommited) and given as follows: *Controller* sends: 18+8\**m* bits, *Target* sends: 2+*m* bits, in **total:** 20+9\**m* bits are transmitted.

### Transmission Speed for set/get Position/Velocity
For the transmissions (get/set Position/Velocity) in questions float values of 4 byte size are transmitted:
|      |Write Bytes *m*|Read Bytes *n*| Total Bytes | Total Bits |
| ---- | ----: | ----: | ----: |  ----: | 
|`setPosition()`/`setVelocity()`| target [float]  4   | flags [uint8_t]  1   | 5 | 75 |
|`getPosition()`/`getVelocity()`|   0   |  value [float] + flags [uint8_t] 4 + 1   | 5 | 75 |

**Table 2:** Number of bytes and bits transmitted per function.

At the '*Standard Mode*' speed of 100 kbit/s the transmission of 75 bits takes then: **$t_{trans}$ = 750 μs** <br>
At the '*Fast Mode*' speed of 400 kbit/s the transmission of 75 bits takes then: **$t_{trans}$ = 187.5 μs**

## Total Execution time
The total execution time $t_{total}$ which was measured in the realtime-test is the sum of of the following contributions:
- Transmission $t_{trans}$: The formerly calculated theoretical tranmission time via I2C.
- Firmware execution time $t_{exec}$: The duration between receiving the command on the firmware, processing it in the `non_blocking_handler()` returning the state flags.
- Overhead $t_{oh}$: Similar to $t_{exec}$, program overhead, for example memory allocation or similar.
- Noise $t_{noise}$: Delays outside the programs control, for example preemptions.

$$
t_{total} = t_{trans} + t_{exec} + t_{oh} +t_{noise}
$$

## Tests
A series of individual tests have been conducted to gather the relevant data to determine the contributing factors described in the previous section.
- set/getPosition at 100 kHz
    - File: *[position_100khz.csv](position_100kHz.csv)*
- set/getPosition at 400 kHz
    - File: *[position_400khz.csv](position_400kHz.csv)*
- set/getVelocity at 100 kHz
    - File: *[velocity_100khz.csv](velocity_100kHz.csv)*
- set/getVelocity at 400 kHz
    - File: *[velocity_400khz.csv](velocity_400kHz.csv)*
- set/getPosition at 400 kHz, execution time on firmware.
    - File: *[baseline_joint_400khz.csv](baseline_joint_400kHz.csv)*

Addtionally the I2C waveform on the SDA and SCL line has been measured with an oscilloscope to judge if the Raspberry Pi 4 is capable of driving the bus with the given cable length at 400 kHz.
## Results
### Total Time
<table>
  <tr>
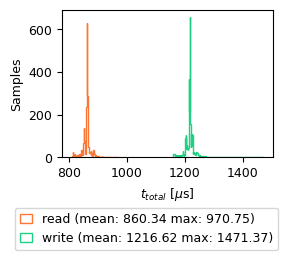
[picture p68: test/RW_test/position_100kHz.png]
    <td><center><strong>Figure 1(a):</strong> Histogram of total time of get/setPosition() at 100 kHz</td>
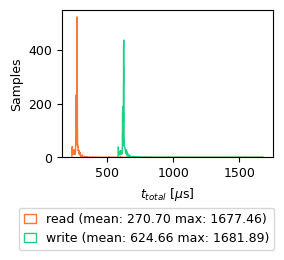
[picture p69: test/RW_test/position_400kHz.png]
    <td><center><strong>Figure 1(b):</strong> Histogram of total time of get/setPosition() at 400 kHz</td>
  </tr>
   <tr>
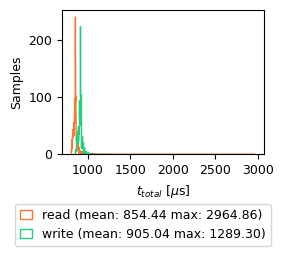
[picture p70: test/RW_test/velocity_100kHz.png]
    <td><center><strong>Figure 1(c):</strong> Histogram of total time of get/setVelocity() at 100 kHz</td>
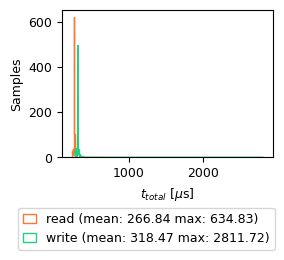
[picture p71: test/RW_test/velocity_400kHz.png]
    <td><center><strong>Figure 1(d):</strong> Histogram of total time of get/setVelocity() at 400 kHz</td>
  </tr>
</table>

<br> 

The results are summarized in Table 3 below:
| Speed Mode [kHz] |Function   | Mean [μs] | Max [μs]    |
| ---- | ---- | ----: | ----: |
|100|`getPosition()`|860.34 | 970.75|
||`setPosition()`| 1216.62|1471.37|
||`getVelocity()`| 854.44 | 2964.86|
||`setVelocity()`| 905.04|2964.86|
|  |  |  |  |
|400|               `getPosition()`| 270.70 | 1677.46|
||            `setPosition()`   | 624.66|1681.89|
||            `getVelocity()`   | 266.84 | 634.83|
||            `setVelocity()`   | 318.47|2811.72|

**Table 3:** Mean and Max total time $t_{total}$ at different transmission speeds and for velocity and position

There is an interesting feature: The `setPosition()` method takes significantly longer than all other functions at a given speed. Furthermore the difference between mean total time for `setPosition()` and `getPosition()` at 100 kHz and 400 kHz is 357 μs and 354 μs respectively, basically identical regardless of the transmission speed. All other functions are somewhat equally fast at their repective transmission speed.

### Execution Time on Firmware
The test was conducted at 400 kHz, however this has no effect since the test only times the execution time between transmission parts.

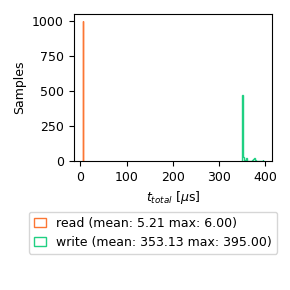
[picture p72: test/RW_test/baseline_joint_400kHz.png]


**Figure 2:** Histogram of the execution time of the position set and get method on the firmware.

This test clearly shows the reason for the much longer $t_{total}$ for `setPosition()`: The corresponding function on the joint firmware itself takes on average $t_{exec}$ = 353.13 μs, while the corresponding function to `getPosition()` only takes  $t_{exec}$ = 5.21 μs on average, exactly the difference previously described. The execution on the joint takes hence 345.92 μs longer, very close the discrepancy in $t_{total}$.

There is no data for the $t_{exec}$ for `setVelocity()` and  `getVelocity()`, however from the total time it can be deduced that the execution time is similar to $t_{exec}$ for `getPosition()`, since they are relatively close.

this leaves finally the calculation of overhead and noise:<br>
$$
t_{oh} + t_{noise}  = t_{total} - t_{exec} - t_{trans} 
$$

|Speed |Methods|$t_{oh} + t_{noise}$ [μs]|
|---|---|---:|
|100|`getPosition()`|105|
||`setPosition()`|113|
||||
|400|`getPosition()`|84|
||`setPosition()`|78|

**Table 4:** Noise and overhead calculation results.

Table 4 shows that the calculated noise and overhead are only to little degree dependent on transmission speed, and remain somewhat constant. This is expected for the software overhead.

### I2C Waveform
The Inter-Integrated-Circuit (I2C) protocol was as the name suggest never designed to communicate over long distances, however in this applications the wire length accumulates to around 4 m. The long cable length introduces a large capacitance which has to be driven by the Raspberry Pis 1.8 kΩ pul-up resistors. The faster the I2C speed the faster the charge has to be removed and applied, if the capacitance is too large the waveform will become distorted, and in the worst case when the bit value is read, it has not yet reached the HIGH or LOW value.

The oscilloscope screen captures show that the waveform at 400 kHz already looks distorted but crucially the SDA seems to reach the HIGH/LOW state when the SCL signal becomes high. It is at this point the bit is sampled as 0 or 1. From this analysis it is concluded that the I2C bus could be driven at 400 kHz.

<table>
  <tr>
    <td><center><strong>Figure 3(a):</strong> Waveform of SCL (blue) and SDA (yellow) of the I2C bus 100 kHz</td>
  </tr>
   <tr>
    <td><center><strong>Figure 3(b):</strong> Waveform of SCL (blue) and SDA (yellow) of the I2C bus 400 kHz</td>
  </tr>
</table>

There are two limitations: 
- The oscilloscope has a too low sampling frequency to judge the 400 kHz waveform correctly
- The potential result driving the bus at 400 kHz could be a bit flip, which could would go unchecked since no checksum is implemented in the communication protocol to save bytes. A bit flip could have destructive results.

## Discussion
This test has been conducted to investigate if it is possible to increase the controller frequency to achieve better performance and to determine if velocity control is feasible.

### Velocity based Control
This controller relies on a closed loop feedback and calculates joint velocity commands through a PID loop. This has the advantage that it eliminates tracking error for ramp inputs. See the [tracking_error test](../tracking_error/README.md). For this reason the velocity controller is preferential, but it requires a higher controller frequency for a given joint speed to be able timely compute new velocity commands.

The controller needs to:
- Read:
  - Joint velocity
  - Joint position
- Write:
  - Joint velocity

| Method            | $t_{total}$ (100 kHz) [μs]| $t_{total}$ (400 kHz) [μs]|
| ---               |---:   |---:   |
|`setVelocity()`        | 905  |319  |
|`getVelocity()`        | 854  |267  |
|`getPosition()`        | 860  | 625  |
| per joint *subtotal*        | 2,619  |1,211  |
| 4 joint **total** | 10,472 | 4,844  |

**Table 5:** Expected total times for the velocity based controller.

### Position based Control
The simplest joint controller simply forwards position commands to the hardware. The controller is non as such since there is no feedback loop. This drastically lightens the requirements on the robot controllers realtime capability and controllers update frequency. However it leaves all the closed loop control to the joint firmware which has a much less advanced internal control loop. This results in a steady state tracking error for a ramp position reference.

The controller needs to:
- Read:
  - Joint position
- Write:
  - Joint position

| Method            | $t_{total}$ (100 kHz) [μs]| $t_{total}$ (400 kHz) [μs]|
| ---               |---:   |---:   |
|`setPosition()`        |  1,217  |625  |
|`getPosition()`        | 860  | 271  |
| per joint *subtotal*        |2,077|896|
| 4 joint **total** |8,308|3,584|

**Table 6:** Expected total times for the position based controller.

### Scheduler Priority
The comm_speed_test program is run without realtime priorities and hence can be subject to preemption of higher priority threads. This will have an impact on worst case execution times but over 1000 samples the impact will be reduced. For this reason the max values have not been taken into consideration. It is assumed that they will be drastically reduced when running with a realtime priority, which the ros2_control node is.

### Final Discussion on I2C Bus speed
Although it is possible to run at 400 kHz I2C bus speed, long term reliability tests are still outstanding to proove that no communication errors occur. For now the I2C speed remains at the much more robust 100 kHz.

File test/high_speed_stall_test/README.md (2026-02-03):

# High speed Stall Detection
This test is to examine the performance of the speed adaptive stall threshold.

> [!Note]
> All values are in motor units, not joint units!

## Test
For an unloaded joint motor, sweep the velocity setpoint slowly from 0 to 120 rad/s and back. The joint firmware prints all metrics of intererst in CSV format to the serial port from where they can be recorded into a file.

## Results
<table>
  <tr>
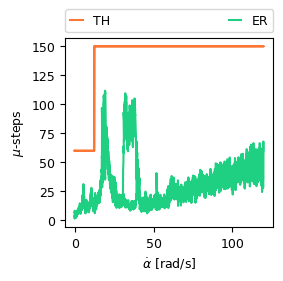
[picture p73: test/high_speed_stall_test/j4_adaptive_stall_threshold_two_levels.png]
    <td><center><strong>Figure 1(a):</strong> Simple two level threshold</td>
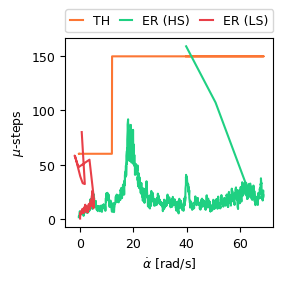
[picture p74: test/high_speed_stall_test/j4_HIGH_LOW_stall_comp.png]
    <td><center><strong>Figure 1(b):</strong> Simple two level threshold with a high speed and low speed stall</td>
  </tr>
</table>

## Development Notes
- Spikey PID error makes problems. First remove large spikes, then fast LP filter to remove remaining spikes of smaller amplitude. Needs to be fast in particular in low speed regime difficult to detect stall. 
- Two regimes with a breakpoint before the "resonance". Reason for systematic increase in PID error in speeds between 15 rad/s and 40 rad/s is unclear. Peak at higher speeds only appears when decelerating.
- Tuning the breakpoint might be necessary but it is difficult since all other joints cant move freely. 
- Threshold is set relatively high, making threshold linear to speed as well has little impact at high threshold values.
- High speed threshold leaves plenty of room. Also when stalling in highspeed regime threshold is pulled down.
- SG_RESULT did not indicate stall, further tuning would be necessary but it would also suffer from limited range.

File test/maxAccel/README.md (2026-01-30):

# Finding the maximum acceleration and deceleration values.
This test assumes no payload.
This test uses the *system_test_packages/max_accel_test/* executable to drive a joint with increasing accelerations and velocities until it can no longer follow.
The data is recorded into a CSV file.

> [!WARNING]
> The executable node is very crude and does not contain protections against crashing into joint limits. 
> Use with care!

Generally max acceleration is more subtle than max vel. in the latter the joint stops moving,
Both values can be increased with higher drive currents.

## J1
- hearable skipping when a max at 3/rad/s2
- first signs of degradation at 3rad/s2 and 1 rad/s.
- at 3rad/s2 and 2rad/s joint doesnt reach max velocity

    -> **vmax** = 1 rad/s; **amax** = 2 rad/s2

## J2
- Higher current to allow faster movement. 50%
- Max velocity at 50% current: 0.03 m/s
- At acceleration > 0.2 rad/s2 acceleration drops to 0.08 rad/s2

    -> **vmax** = 0.03 m/s; **amax** = 0.2 m/s2

## J3
- Max velocity determined to be 5 rad/s at 20% current. (run j3_15)
- max accleration at 14 rad/s2 (run j3_17)
- acc 15 rad/s2 and vel 5rad/s didnt work (run j3_18)

    -> **vmax** = 5 rad/s; **amax** = 14 rad/s2

### J4
- Max acceleration between 30 and 34 rad/s (run j4_3 and j4_4)
- Max veloctiy between 10 and 20 rad/s (run j4_5)
- cant test higher velocities as range is insufficient at given acceleration

    -> **vmax** = 10 rad/s; **amax** = 30 rad/s2

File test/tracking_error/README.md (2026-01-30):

# Quantifying the tracking error
This test is to quantify the tracking errors of position inputs with focus on ramp (constant velocity) reference.
The test compares the performance between the JTC with position as command interface and the JTC with velocity as command interface.

## Assumption
Since the postion JTC simply forwards the postion reference to the joint it can be proven using control theory that any ramp reference will have a bounded non-zero steady state error. However when using the velocity JTC the ramp tracking error will be zero since the position error is mapped through a PID controller with feed-forward to the system which takes the velocity as command input. This way the system has one additional integrator which eliminates the ramp following error.

## Tests
Joint 1 is used for all tests. All generated ramps are below the maximum joint speed, which is constant and configured to be 1.0 rad/s.
Two ramps are configured with different speeds:

**Ramp 1**: From -1.5707 rad to 1.5707 rad in 20 s. Yielding a ramp gradient/speed ($\dot{r}_{1}$) of 0.15707 rad/s <br>
**Ramp 2**: From -1.5707 rad to 1.5707 rad in 10 s. Yielding a ramp gradient/speed of 0.31415 rad/s

The following data is collected:
*Position Setpoint* ($r_{1}$) and *Joint Position* ($q_{1}$).

The error is defined as:
$$
e_{1} = \frac{r_1-q_1}{\dot{r}_{1}}
$$

To investigate the effect of the maximum acceleration setting the test is repeated for the acceleration values given below. Note that these are the maximum hardware values to protect the joint from stalling. The final motion planning will use lower acceleration values to create trajectories.<br>
**MaxAccel 1**: 0.157 rad/s^2 <br>
**MaxAccel 2**: 1.57 rad/s^2 

### Controller Parameters
The JTC runs with an update rate of 50 Hz.
For the position test no parameters can be tuned, since the controller directly forwards the trajectory. Neither on the firmware side, since there the setPoint intern is forwarded to the stepper driver which. The stepper does **not** operate in field oriented control FOC.

### Expected Result
Tracking error stays constant relative to ramp but depends linearly on maxAccel

## Recording:

```bash
ros2 bag record -e ^\/controller_manager.* -o record_<ramp_gradient>_<maxAccel>_<note>
```
for example: here also */velocity_joint_trajectory_controller/controller_state* is recorded
```bash
ros2 bag record /controller_manager/introspection_data/full /velocity_joint_trajectory_controller/controller_state -o record_0p15707_1p57_j1_vel_p0p0_i0p0_d
0p0_kff1p0
```
recording one long ramp input is sufficient. 

After recording export to CSV:
replay topics with:
```bash
ros2 bag play record_<ramp_gradient>_<maxAccel>_<note> -p
``` 
listen and export topics:
```bash
ros2 topic echo /controller_manager/introspection_data/full --csv > record_<ramp_gradient>_<maxAccel>_<note>.csv
```

## Results
### Test 1, Position JTC
|      | 0.15707 | 0.31415 |
| ---- | ------- | ---- |
| 0.157 | ~0.52   |  ~1.0    |
| 1.57  |  ~0.07 |  ~0.12    |

weird, not what expected, error scales with ramp gradient despite normalizing it

### Test 2, Velocity JTC
Steady-state tracking error is zero, where $k_p > 0$

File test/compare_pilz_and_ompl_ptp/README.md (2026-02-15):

# Comparing Trajectory generation for Point-To-Point Motion between Pilz and OMPL Motion Planner
A test to compare PTP trajectories absent of external constraints between the Pilz Industrial Motion Planner and the OMPL planner.
## Background
The Pilz Industrial Motion Planner (PILZ planner) introduces the new Action/Service *MoveGroupSequenceAction*/*MoveGroupSequenceService*, which allows to concatenate multiple trajectories with an optional blend radius. See the [documentation](https://github.com/moveit/moveit2_tutorials/blob/b0ba2a971d18a024d136ec7b175c7353eb0e02d8/doc/how_to_guides/pilz_industrial_motion_planner/pilz_industrial_motion_planner.rst#sequence-of-multiple-segments) for more details.

The motion sequence is created by individual trajectories for each passed waypoint and subsequently blending them together. Being part of the PILZ planning pipeline the motion sequence has been designed for the use with the one of the PILZ motion planners (planner_id: "LIN","CIRC", and "PTP") in mind. Besides the *planner_id*, the planning request of type *MotionPlanRequest* however also allows, to set the *pipeline_id*. By setting the *pipeline_id* to 'ompl' (the exact name depends on the name the planning pipeline has been given when passed to the move_group on launch) the OMPL motion planner can be invoked to create a sequence segment.

## Problem
The problem arises when the trajectories are being blended. To blend two trajectories ([See how](https://github.com/moveit/moveit2/blob/760277f74ba78bc48f157f7f6c38ac13de4a2721/moveit_planners/pilz_industrial_motion_planner/doc/MotionBlendAlgorithmDescription.pdf)) the first trajectory's last point and second trajectory's first point must have equal position, and zero velocity and acceleration. The PILZ planners create such trajectories, OMPL however do not and hence [this](https://github.com/moveit/moveit2/blob/760277f74ba78bc48f157f7f6c38ac13de4a2721/moveit_planners/pilz_industrial_motion_planner/src/trajectory_blender_transition_window.cpp#L177) fails. Inhibiting the sequence blender to complete successfully. The trajectory created by OMPL however is a trapezoidal trajectory (absent of other constraints like collisions) and hence SHOULD have zero acceleration at the start and end.

## Test
To investigate why the blending fails a simple test is conducted. The robot hardware is launch (mock_hardware is sufficient), the move_group and Rviz with the MotionPlanning panel is started. Using the MotionPlanning a new goal position (relatively close to the starting position to avoid long trajectories) is created and a planning request is sent. First to the OMPL and secondly the the PILZ PTP planner. The planners respond with a created trajectory which is logged and plotted using the [plotting script](../traj_plots/README.md).

## Results
The resulting trajectories as created by the planners are plotted below. 
<table>
  <tr>
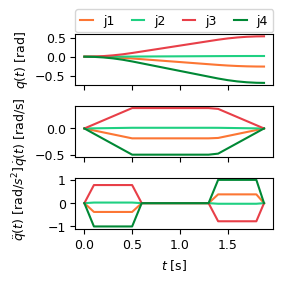
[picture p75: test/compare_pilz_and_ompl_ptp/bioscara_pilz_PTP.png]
    <td><center><strong>Figure 1(a):</strong> Trajectory created by the PILZ PTP planner</td>
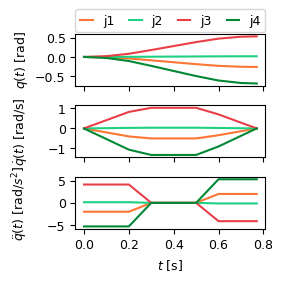
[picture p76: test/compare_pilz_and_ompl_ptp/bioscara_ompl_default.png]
    <td><center><strong>Figure 1(b):</strong> Trajectory created by the OMPL default planner</td>
  </tr>
</table>

There are two striking differences:
1) For the same acceleration and velocity limits the OMPL planner produces a trajectory that takes 0.77 s, while the PILZ PTP trajectory takes 1.88 s.
2) The PILZ trajectory has $\ddot{q} = 0.0$ acceleration at $t = t_0 = 0.0$ s and $t=t_f= 1.88$ s, while the OMPL trajectory has $\ddot{q} \ne 0.0$ acceleration at $t = t_0 = 0.0$ s and $t=t_f= 0.77$ s.

## Discussion
The observation described in (2) is the direct cause for the failing trajectory blend.

The significant execution duration can be attributed to the fact that the PILZ motion planner is choosing a very conservative/non-optimal approach to calculate the trapezoidal trajectory using the strictest [joint limits](https://github.com/moveit/moveit2_tutorials/blob/b0ba2a971d18a024d136ec7b175c7353eb0e02d8/doc/how_to_guides/pilz_industrial_motion_planner/pilz_industrial_motion_planner.rst#joint-limits). This approach guarantees that no kinematic limits are violated, however does so suboptimally, since the existence of a faster trajectory (the OMPL one) satisfying the same joint limits disproves optimality. This suboptimality, combined with the lacking collision avoidance when using the PILZ PTP planner is a key reason the attempt to create a motion sequence with an alternative planner has been undertaken. Ideally it is possible to leverage the convenient blended sequence with the more advanced OMPL planner.

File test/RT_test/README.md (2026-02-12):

# Analyzing Realtime Performance of the Ubuntu Kernel
This test is to analyze the impact of kernel configurations on the execution times of the ros2_control main update loop. Missed deadlines could lead to poor controller performance.

## Approach:
Two test were conducted to evaluate the effect of the control loop's process priority on its execution time and periodicity during which the controller manager's diagnostic */controller_manager/statistics/* output was recorded. One test is conducted with the controller manager node with standard priority and the seocnd with RT priority.
By default the controller manager attempts to run the control loop with a RT priority of 50 and SCHED_FIFO, if it is lacking the rights for this, standard priority 20 and SCHED_OTHER is used. A description of the differeent schedulers and task priorities are given [here](https://man7.org/linux/man-pages/man7/sched.7.html) and [here](https://blogs.oracle.com/linux/post/task-priority).

### System Load:
The system is slightly loaded with the following ssh sessions (no X forwarding):
- ros2_control
- trajectory publisher
- ros2 bag recorder

A simple trajectory is published every 5s on the joint trajectory publisher test node:
```yaml
publisher_joint_trajectory_controller:
  ros__parameters:

    controller_name: "velocity_joint_trajectory_controller"
    wait_sec_between_publish: 15
    time_from_start: 10

    goal_names: ["pos1", "pos2"]
    pos1:
      positions: [-1.5707, 0.2, 0.0, 0.0]
    pos2:
      positions: [1.5707, 0.2, 0.0, 0.0]

    joints:
      - j1
      - j2
      - j3
      - j4

    check_starting_point: false
```
During a 10 minute period the robot executes a simple motion that alternates the J1, J3 and J4 position by 90°. The longer the test can run, the higher the chances to records an uncommon latency, the 10 minute period were chosen as a compromise

### Recording:
The controller manager publishes diagonstic telemetry about its update loop. The topics are recorded into a bag file:
```bash
ros2 bag record -e ^\/controller_manager.* -o record_<update_rate>_<prio>_<note>
```
Each test is conducted over 10 min, to increase the chance of uncommon latencies happening.

After the recording the bag file is replayed and saved to a CSV file:
```bash
ros2 bag play record_<update_rate>_<prio>_<note> -p
``` 
In another terminal listen and export topics to CSV:
```bash
ros2 topic echo /controller_manager/statistics/full --csv > record_<update_rate>_<prio>_<note>.csv
```

### ros2_control configuration
For each test the bioscara_arm hardware component, position_joint_trajectory_controller and joint_state_broadcaster are loaded and active. The controller manager is configured to run at 50 Hz -> 20 ms deadline. The assumption is that increasing scheduler priority shows effect by reducing the total control loop execution time.

## Test 1
The first test is conducted with the controller manager node running a non-realtime priority 20. The recording is 603 seconds long.

## Test 2
The second test is executed with the controller manager node with realtime priority 50 and FIFO Scheduler (default ros2_control values).
The user *scara* user has been added to the realtime group as described in the user manuals.

The recording is 613 seconds long.

## Results
The controller manager's total update loop execution time is the primary analyzed metric. A histogram of its distrbution in the non-RT and RT context is displayed in Figure 1. From the figure it is visible that the assumption of faster execution time is false. The only noticable change is that over the 10 min window the upper bound has decreased, indicating that the process has indeed received higher priority from the scheduler. On the other hand, the lower bound has also increased, for unclear reasons. The overall result is that the standard deviation has decreased.

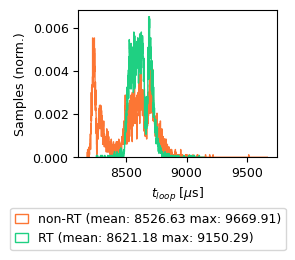
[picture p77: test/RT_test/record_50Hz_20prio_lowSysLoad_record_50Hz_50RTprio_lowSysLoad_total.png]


**Figure 1:** Histogram of the total controller manager control loop in RT and non-RT context.

<table>
  <tr>
    <td><center><strong>Figure 2(a):</strong> Histogram of the exeuction time of the read-phase of the control loop. Split by the contribution from the bioscara_arm hardware interface and the total controller manager (CM) read duration.</td>
    <td><center><strong>Figure 2(b):</strong> Histogram of the exeuction time of the write-phase of the control loop. Split by the contribution from the bioscara_arm hardware interface and the total controller manager (CM) write duration.</td>
    <td><center><strong>Figure 2(b):</strong> Histogram of the total exeuction time of the control loop. Split by the contribution from the bioscara_arm hardware interface (sum of read+write) and the total controller manager (CM) cycle duration.</td>
  </tr>
</table>

## Observation
The plot in figure 1 disproves the assumption, the mean execution is unchanged between the tests, logically so because 8.6 ms is an order of magnitude away from the system latency which is usually at most a few hundred μs. The biggest effect is visible in the standard deviation which has reduced significantly from 187 μs to 75 μs, the lower priority process' wider spread indicates that it gets repeatedly preempted by other tasks, while the process run with RT priority gets prioritized, allowing it to finish in time.

## Discussion

The high mean execution time, far greater than system latency, indicates that there are other factors that throttle the control loop. This prompted a closer investigation of the data. Figure 2b displays another histogram, this time comparing the total loop time with just the sum of the read and write phase of the bioscara_arm hardware component during the same high priority test. The plot shows that the on average 97.8% of total execution time is spent in the hardware's read or write method. The remaining 193 μs are subsequently spent in the trajectory controllers and joint state broadcasters update phase. This insight led to yet another test described in the following section which reveals that the I2C communication is the bottleneck that slows down the control loop. This is also the reason why more controllers or even the gripper hardware component, which does not rely on I2C, would presumably have little impact on the test results.


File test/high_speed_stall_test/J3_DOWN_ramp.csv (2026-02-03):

Program Time [s] | raw abs(pid-error) | abs(pid-error) spikes removed | abs(pid-error) spikes removed LP filtered | raw SG_RESULT | SG_RESULT spikes removed | q [deg] | q_set [deg] | qd [rad/s] | qd_set [rad/s] | threshold | stall
29.5795 | 9 | 9 | 9.8 | 0 | 0 | 0 | 0 | -0 | 0.6 | 60 | 0
29.5894 | 9 | 9 | 9.64 | 0 | 0 | 0 | 0 | -0 | 0.6 | 60 | 0
29.5996 | 9 | 9 | 9.51 | 0 | 0 | 0 | 0 | -0 | 0.6 | 60 | 0
29.6096 | 9 | 9 | 9.41 | 0 | 0 | 0 | 0 | -0 | 0.6 | 60 | 0
29.6198 | 10 | 10 | 9.53 | 0 | 0 | 0 | 0 | -0 | 0.6 | 60 | 0
29.6297 | 10 | 10 | 9.62 | 0 | 0 | 0 | 0 | -0 | 0.6 | 60 | 0
29.6394 | 10 | 10 | 9.7 | 0 | 0 | 0 | 0 | -0 | 0.6 | 60 | 0
29.6494 | 9 | 9 | 9.56 | 0 | 0 | 0 | 0 | -0 | 0.6 | 60 | 0
29.6593 | 9 | 9 | 9.45 | 0 | 0 | 0 | 0 | -0 | 0.6 | 60 | 0
29.6695 | 9 | 9 | 9.36 | 0 | 0 | 0 | 0 | -0 | 0.6 | 60 | 0
29.6795 | 10 | 10 | 9.49 | 0 | 0 | 0 | 0 | -0 | 0.6 | 60 | 0
29.6896 | 10 | 10 | 9.59 | 0 | 0 | 0 | 0 | -0 | 0.6 | 60 | 0
29.6995 | 9 | 9 | 9.47 | 0 | 0 | 0 | 0 | -0 | 0.6 | 60 | 0
29.7096 | 9 | 9 | 9.38 | 0 | 0 | 0 | 0 | -0 | 0.6 | 60 | 0
29.7197 | 10 | 10 | 9.5 | 0 | 0 | 0 | 0 | -0 | 0.6 | 60 | 0
29.7296 | 10 | 10 | 9.6 | 0 | 0 | 0 | 0 | -0 | 0.6 | 60 | 0
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

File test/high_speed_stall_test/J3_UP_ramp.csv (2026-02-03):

Program Time [s] | raw abs(pid-error) | abs(pid-error) spikes removed | abs(pid-error) spikes removed LP filtered | raw SG_RESULT | SG_RESULT spikes removed | q [deg] | q_set [deg] | qd [rad/s] | qd_set [rad/s] | threshold | stall
5702.85 | 8 | 8 | 6.96 | 0 | 0 | 0 | 0 | 0 | 0 | 60 | 0
5702.86 | 8 | 8 | 7.17 | 0 | 0 | 0 | 0 | 0 | 0 | 60 | 0
5702.87 | 5 | 5 | 6.73 | 0 | 0 | 0 | 0 | 0 | 0 | 60 | 0
5702.88 | 5 | 5 | 6.39 | 0 | 0 | 0 | 0 | 0 | 0 | 60 | 0
5702.89 | 8 | 8 | 6.71 | 0 | 0 | 0 | 0 | 0 | 0 | 60 | 0
5702.9 | 7 | 7 | 6.77 | 0 | 0 | 0 | 0 | 0 | 0 | 60 | 0
5702.91 | 8 | 8 | 7.01 | 0 | 0 | 0 | 0 | 0 | 0 | 60 | 0
5702.92 | 8 | 8 | 7.21 | 0 | 0 | 0 | 0 | -0 | 0 | 60 | 0
5702.93 | 7 | 7 | 7.17 | 0 | 0 | 0 | 0 | -0 | 0 | 60 | 0
5702.94 | 7 | 7 | 7.14 | 0 | 0 | 0 | 0 | -0 | 0 | 60 | 0
5702.95 | 7 | 7 | 7.11 | 0 | 0 | 0 | 0 | -0 | 0 | 60 | 0
5702.96 | 5 | 5 | 6.69 | 0 | 0 | 0 | 0 | -0 | 0 | 60 | 0
5702.97 | 5 | 5 | 6.35 | 0 | 0 | 0 | 0 | -0 | 0 | 60 | 0
5702.98 | 7 | 7 | 6.48 | 0 | 0 | 0 | 0 | 0 | 0 | 60 | 0
5702.99 | 7 | 7 | 6.58 | 0 | 0 | 0 | 0 | 0 | 0 | 60 | 0
5703 | 7 | 7 | 6.67 | 0 | 0 | 0 | 0 | 0 | 0 | 60 | 0
5703.01 | 7 | 7 | 6.73 | 0 | 0 | 0 | 0 | 0 | 0 | 60 | 0
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

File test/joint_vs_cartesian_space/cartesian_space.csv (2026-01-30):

__time | /velocity_joint_trajectory_controller/controller_state/error/positions[0] | /velocity_joint_trajectory_controller/controller_state/error/positions[1] | /velocity_joint_trajectory_controller/controller_state/error/positions[2] | /velocity_joint_trajectory_controller/controller_state/error/positions[3] | /velocity_joint_trajectory_controller/controller_state/error/time_from_start/nanosec | /velocity_joint_trajectory_controller/controller_state/error/time_from_start/sec | /velocity_joint_trajectory_controller/controller_state/error/velocities[0] | /velocity_joint_trajectory_controller/controller_state/error/velocities[1] | /velocity_joint_trajectory_controller/controller_state/error/velocities[2] | /velocity_joint_trajectory_controller/controller_state/error/velocities[3] | /velocity_joint_trajectory_controller/controller_state/feedback/positions[0] | /velocity_joint_trajectory_controller/controller_state/feedback/positions[1] | /velocity_joint_trajectory_controller/controller_state/feedback/positions[2] | /velocity_joint_trajectory_controller/controller_state/feedback/positions[3] | /velocity_joint_trajectory_controller/controller_state/feedback/time_from_start/nanosec |
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

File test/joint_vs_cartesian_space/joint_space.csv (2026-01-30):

__time | /velocity_joint_trajectory_controller/controller_state/error/positions[0] | /velocity_joint_trajectory_controller/controller_state/error/positions[1] | /velocity_joint_trajectory_controller/controller_state/error/positions[2] | /velocity_joint_trajectory_controller/controller_state/error/positions[3] | /velocity_joint_trajectory_controller/controller_state/error/time_from_start/nanosec | /velocity_joint_trajectory_controller/controller_state/error/time_from_start/sec | /velocity_joint_trajectory_controller/controller_state/error/velocities[0] | /velocity_joint_trajectory_controller/controller_state/error/velocities[1] | /velocity_joint_trajectory_controller/controller_state/error/velocities[2] | /velocity_joint_trajectory_controller/controller_state/error/velocities[3] | /velocity_joint_trajectory_controller/controller_state/feedback/positions[0] | /velocity_joint_trajectory_controller/controller_state/feedback/positions[1] | /velocity_joint_trajectory_controller/controller_state/feedback/positions[2] | /velocity_joint_trajectory_controller/controller_state/feedback/positions[3] | /velocity_joint_trajectory_controller/controller_state/feedback/time_from_start/nanosec |
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

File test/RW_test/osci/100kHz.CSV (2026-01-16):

SCL | SDA | 1.0uS
175 | 178
174 | 178
182 | 182
180 | 185
184 | 184
181 | 185
184 | 185
181 | 185
184 | 185
181 | 185
185 | 184
182 | 186
184 | 185
180 | 186
184 | 184
180 | 185
182 | 184
179 | 185
182 | 184
180 | 185
182 | 184
179 | 184
184 | 184
179 | 184
184 | 184
181 | 185
184 | 184
181 | 185
184 | 182
181 | 185
184 | 183
180 | 184
182 | 184
179 | 184
181 | 182
179 | 185
182 | 182
179 | 184
182 | 182
181 | 185
184 | 184
181 | 185
185 | 184
183 | 185
185 | 184
182 | 184
184 | 183
180 | 185
182 | 183
179 | 184
182 | 183
178 | 184
182 | 182
179 | 184
182 | 182
180 | 184
184 | 184
181 | 185
185 | 184
182 | 185
185 | 184
182 | 185
184 | 184
181 | 185
183 | 182
180 | 184
182 | 182
179 | 184
182 | 182
179 | 184
182 | 182
179 | 184
182 | 184
180 | 185
184 | 184
181 | 185
185 | 184
181 | 185
184 | 184
181 | 185
184 | 182
181 | 185
182 | 182
180 | 184
182 | 182
179 | 184
184 | 184
179 | 185
183 | 184
181 | 187
184 | 184
181 | 185
184 | 184
181 | 185
184 | 184
181 | 185
184 | 182
181 | 184
183 | 182
179 | 184
184 | 182
179 | 184
182 | 182
179 | 184
182 | 182
179 | 184
184 | 185
181 | 187
182 | 182
181 | 184
185 | 184
181 | 185
182 | 182
181 | 184
182 | 184
180 | 184
182 | 182
179 | 184
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

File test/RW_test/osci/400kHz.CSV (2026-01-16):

SCL | SDA | 1.0uS
172 | 175
173 | 176
181 | 182
178 | 184
182 | 182
179 | 184
183 | 182
181 | 184
184 | 184
181 | 185
184 | 184
181 | 184
184 | 184
180 | 184
182 | 183
179 | 184
182 | 184
179 | 184
182 | 182
179 | 184
182 | 182
179 | 184
182 | 182
181 | 184
184 | 182
181 | 184
184 | 182
180 | 184
184 | 184
180 | 184
182 | 182
179 | 184
182 | 182
179 | 184
182 | 182
179 | 184
182 | 182
179 | 184
184 | 184
181 | 184
184 | 183
181 | 184
184 | 184
180 | 184
182 | 182
181 | 184
184 | 182
179 | 185
182 | 182
179 | 184
182 | 182
181 | 184
182 | 182
180 | 184
183 | 182
180 | 184
182 | 182
181 | 185
182 | 182
180 | 184
182 | 182
179 | 184
182 | 184
181 | 184
184 | 182
180 | 184
182 | 182
180 | 184
182 | 182
180 | 185
184 | 184
181 | 184
182 | 183
180 | 184
184 | 183
180 | 184
182 | 183
180 | 184
182 | 182
179 | 184
182 | 183
179 | 184
182 | 182
180 | 185
184 | 182
181 | 185
185 | 184
182 | 185
185 | 184
182 | 185
185 | 185
181 | 185
182 | 182
179 | 184
182 | 182
179 | 184
182 | 182
179 | 185
182 | 182
179 | 184
182 | 182
179 | 184
184 | 183
181 | 185
185 | 185
182 | 186
184 | 184
179 | 182
183 | 182
181 | 184
182 | 184
180 | 185
182 | 183
179 | 184
182 | 182
179 | 184
182 | 184
179 | 184
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

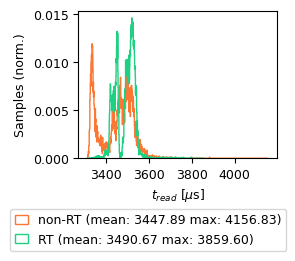
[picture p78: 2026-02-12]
test/RT_test/record_50Hz_20prio_lowSysLoad_record_50Hz_50RTprio_lowSysLoad_read.png

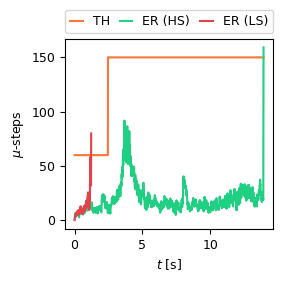
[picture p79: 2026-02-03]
test/high_speed_stall_test/j4_HIGH_LOW_stall_comp_ts.png

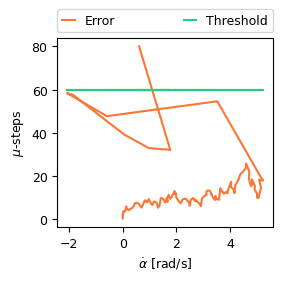
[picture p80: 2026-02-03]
test/high_speed_stall_test/j4_LOW_SPEED_STALL_adaptive_stall_threshold_two_levels.png

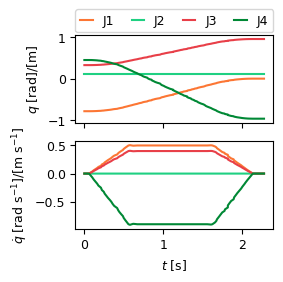
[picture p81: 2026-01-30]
test/joint_vs_cartesian_space/joint_space.png

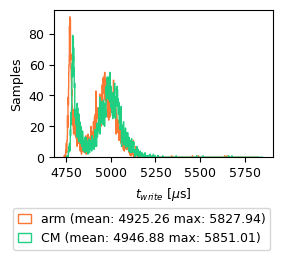
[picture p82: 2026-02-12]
test/RT_test/record_50Hz_20prio_lowSysLoad_write.png

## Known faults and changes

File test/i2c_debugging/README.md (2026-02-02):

**sample1:**

i2cget -y 1 0x11 0x0f

"main" firmware (no test) at https://github.com/DALSA-Lab/bioscara/blob/bce66ca3f7d215edcba7416d0361210beb87d8f3/Arduino/joint/joint.ino

using i2c-gpio overlay (hardware i2c disabled):

```plain
dtoverlay=i2c-gpio,bus=1,i2c_gpio_sda=2,i2c_gpio_scl=3,i2c_gpio_delay_us=2
```

Only j1 connected

Observations:

- Yellow (chB): SDA, Blue (chA): SCL
- Visible crosstalk on every large transition
- AND: clock stretching
- Time divisions are not correct. Measured on osci is 6 us period
- Frequency: 138kHz
- short SDA spike:
  - ACK after address?
  - COntroller releases SDA and waits for answer?
  - Has been osbserved multiple times (not a glitch)

**Sample 2**

same firmware and data request. This time 

```
dtparam=i2c_arm=on,i2c_arm_baudrate=100000
```

hardware i2c

 Observations:

- Same cross coupling obvs.
- slower
- 100 kHz

## Generally

All samples exhibit crosstalk, a potential culprit for a stuck bus according to the [TI Application Note](https://www.ti.com/lit/an/scpa069/scpa069.pdf?ts=1768568213636). It mentions that if a bus exhibits crosstalk, although mostly present on SDA, a false SCL edge can be triggered on the start condition. Indeed both samples exhibit also a "dip" in SCL at the start condtion when SDA gets pulled low.

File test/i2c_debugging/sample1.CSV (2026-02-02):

 |  | CH1 1.0V | CH2 1.0V | 2.0uS
; |  | Probe:X1 | Probe:X1
83 | 175 | 83 | 75
81 | 177 | 81 | 77
92 | 184 | 92 | 84
88 | 185 | 88 | 85
94 | 185 | 94 | 85
89 | 187 | 89 | 87
93 | 185 | 93 | 85
90 | 186 | 90 | 86
93 | 185 | 93 | 85
89 | 187 | 89 | 87
93 | 185 | 93 | 85
90 | 187 | 90 | 87
93 | 185 | 93 | 85
89 | 187 | 89 | 87
93 | 185 | 93 | 85
89 | 185 | 89 | 85
93 | 184 | 93 | 84
89 | 187 | 89 | 87
92 | 185 | 92 | 85
89 | 186 | 89 | 86
93 | 185 | 93 | 85
89 | 186 | 89 | 86
93 | 184 | 93 | 84
89 | 185 | 89 | 85
93 | 184 | 93 | 84
89 | 185 | 89 | 85
93 | 185 | 93 | 85
89 | 185 | 89 | 85
93 | 185 | 93 | 85
89 | 186 | 89 | 86
93 | 184 | 93 | 84
89 | 187 | 89 | 87
93 | 185 | 93 | 85
89 | 185 | 89 | 85
93 | 185 | 93 | 85
89 | 185 | 89 | 85
93 | 185 | 93 | 85
89 | 186 | 89 | 86
93 | 184 | 93 | 84
89 | 187 | 89 | 87
93 | 185 | 93 | 85
89 | 187 | 89 | 87
93 | 184 | 93 | 84
90 | 186 | 90 | 86
93 | 185 | 93 | 85
89 | 187 | 89 | 87
93 | 185 | 93 | 85
89 | 186 | 89 | 86
93 | 185 | 93 | 85
89 | 186 | 89 | 86
93 | 184 | 93 | 84
89 | 185 | 89 | 85
93 | 185 | 93 | 85
89 | 187 | 89 | 87
93 | 184 | 93 | 84
89 | 186 | 89 | 86
93 | 185 | 93 | 85
89 | 186 | 89 | 86
93 | 185 | 93 | 85
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

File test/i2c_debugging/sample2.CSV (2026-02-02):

 |  | CH1 1.0V | CH2 1.0V | 2.0uS
; |  | Probe:X1 | Probe:X1
84 | 176 | 84 | 76
81 | 176 | 81 | 76
92 | 184 | 92 | 84
89 | 186 | 89 | 86
93 | 185 | 93 | 85
90 | 187 | 90 | 87
95 | 185 | 95 | 85
90 | 187 | 90 | 87
95 | 186 | 95 | 86
90 | 188 | 90 | 88
94 | 185 | 94 | 85
90 | 188 | 90 | 88
94 | 185 | 94 | 85
90 | 187 | 90 | 87
94 | 185 | 94 | 85
89 | 187 | 89 | 87
93 | 185 | 93 | 85
89 | 187 | 89 | 87
93 | 185 | 93 | 85
90 | 186 | 90 | 86
93 | 185 | 93 | 85
89 | 186 | 89 | 86
93 | 184 | 93 | 84
90 | 187 | 90 | 87
93 | 185 | 93 | 85
90 | 187 | 90 | 87
93 | 185 | 93 | 85
89 | 187 | 89 | 87
94 | 185 | 94 | 85
89 | 187 | 89 | 87
94 | 185 | 94 | 85
90 | 187 | 90 | 87
93 | 185 | 93 | 85
89 | 186 | 89 | 86
94 | 185 | 94 | 85
90 | 187 | 90 | 87
93 | 185 | 93 | 85
90 | 187 | 90 | 87
94 | 185 | 94 | 85
90 | 187 | 90 | 87
93 | 185 | 93 | 85
90 | 187 | 90 | 87
93 | 185 | 93 | 85
89 | 187 | 89 | 87
93 | 185 | 93 | 85
90 | 187 | 90 | 87
93 | 185 | 93 | 85
90 | 186 | 90 | 86
94 | 185 | 94 | 85
89 | 186 | 89 | 86
93 | 185 | 93 | 85
91 | 186 | 91 | 86
93 | 185 | 93 | 85
90 | 187 | 90 | 87
95 | 186 | 95 | 86
90 | 187 | 90 | 87
94 | 185 | 94 | 85
89 | 187 | 89 | 87
93 | 185 | 93 | 85
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

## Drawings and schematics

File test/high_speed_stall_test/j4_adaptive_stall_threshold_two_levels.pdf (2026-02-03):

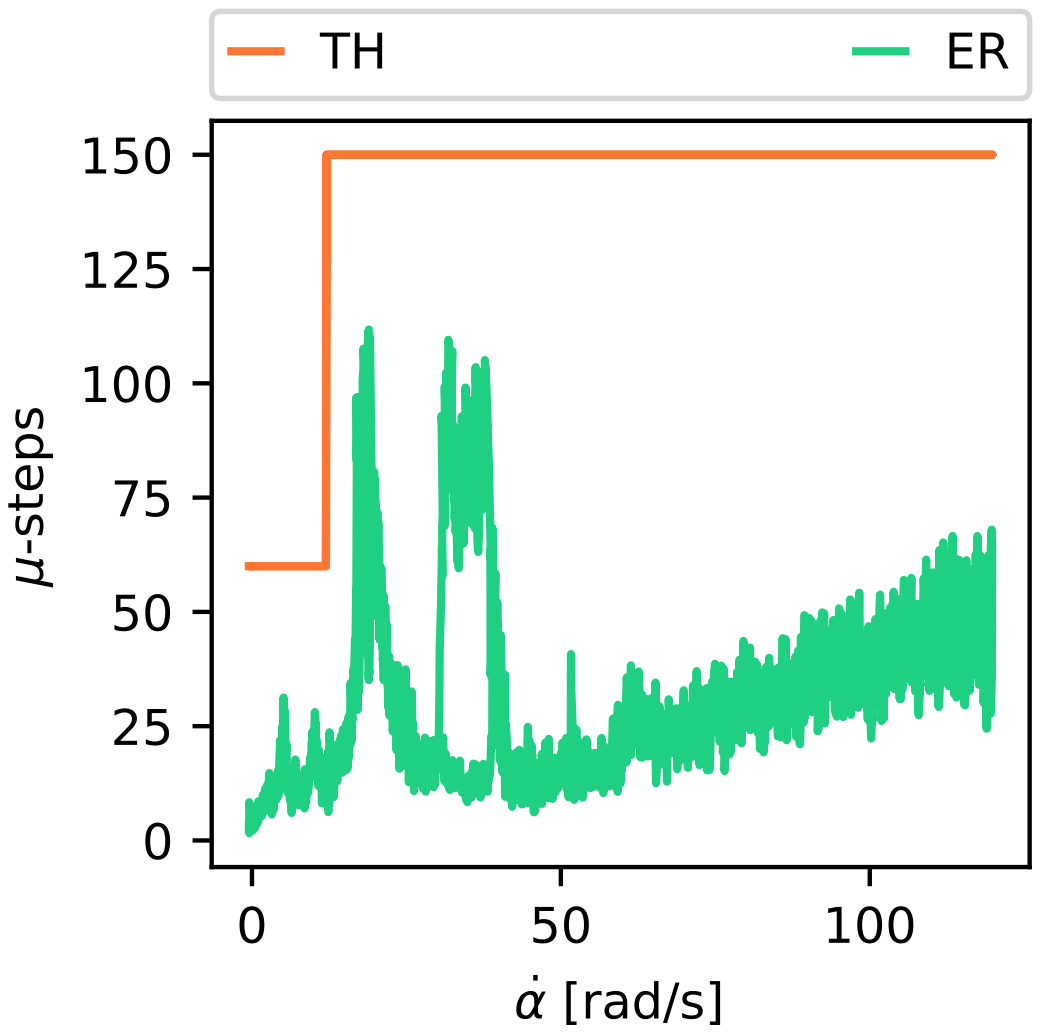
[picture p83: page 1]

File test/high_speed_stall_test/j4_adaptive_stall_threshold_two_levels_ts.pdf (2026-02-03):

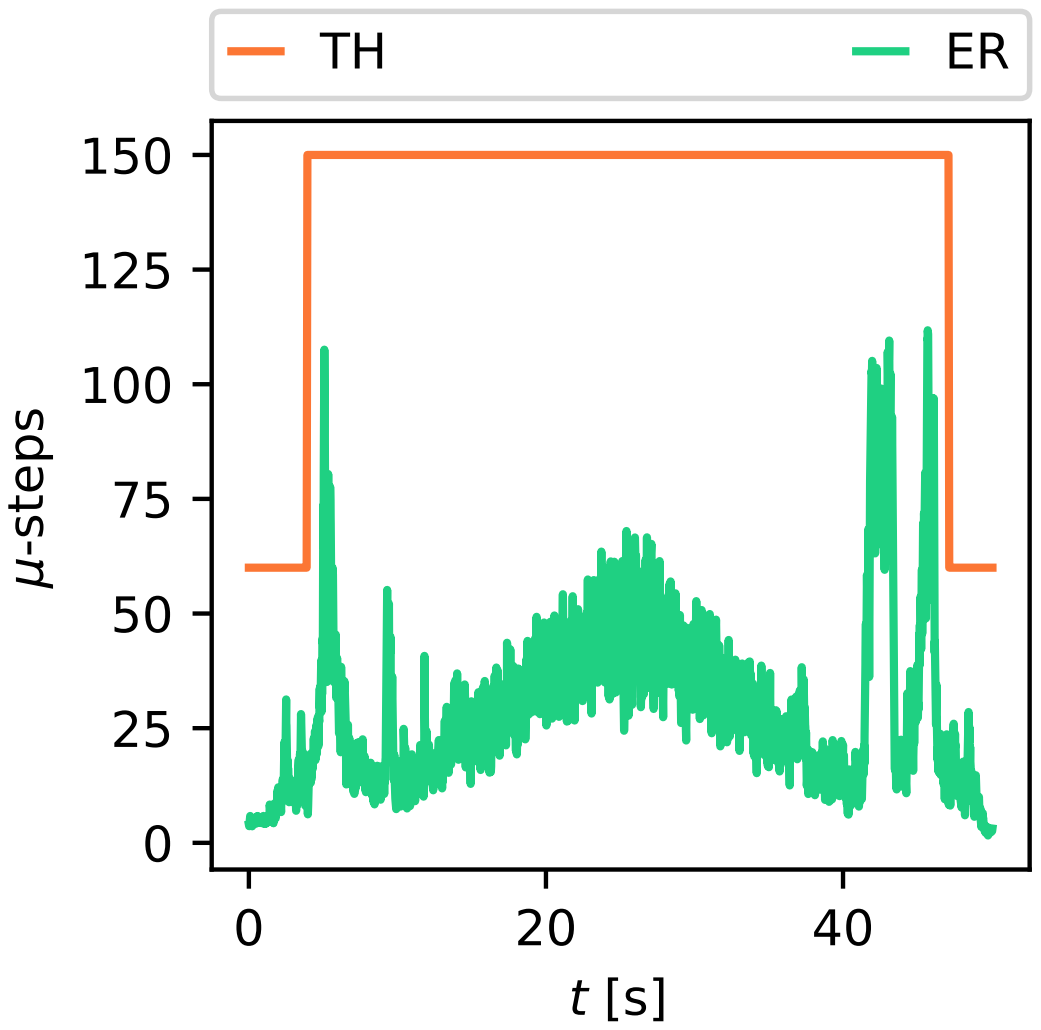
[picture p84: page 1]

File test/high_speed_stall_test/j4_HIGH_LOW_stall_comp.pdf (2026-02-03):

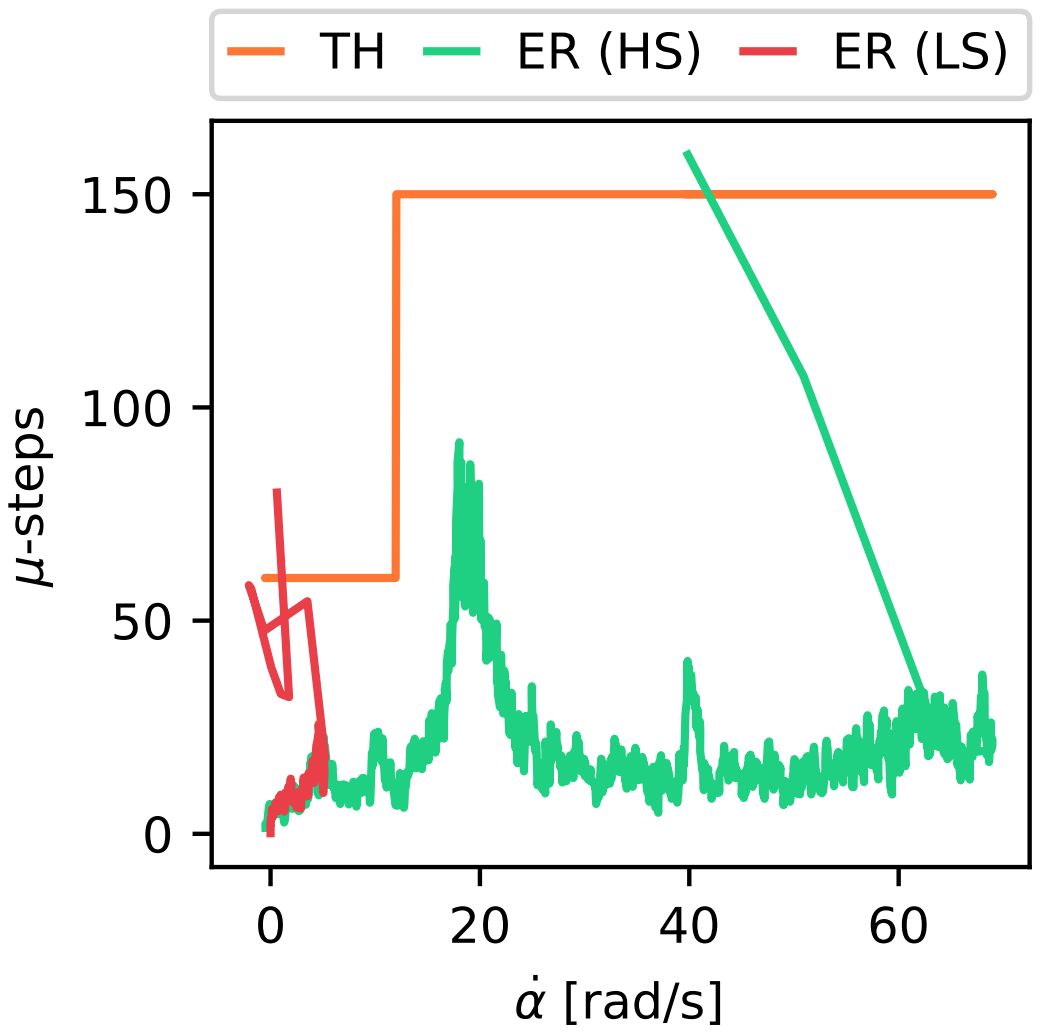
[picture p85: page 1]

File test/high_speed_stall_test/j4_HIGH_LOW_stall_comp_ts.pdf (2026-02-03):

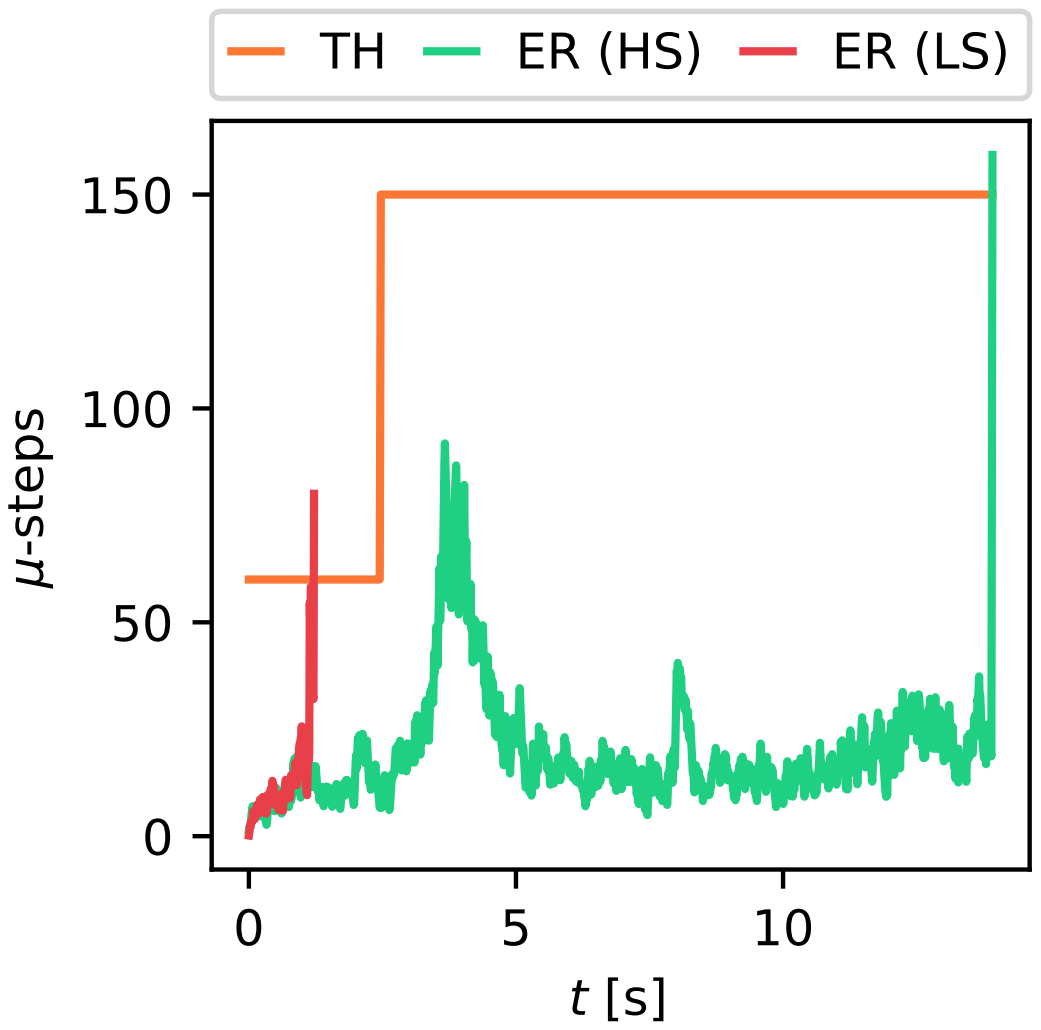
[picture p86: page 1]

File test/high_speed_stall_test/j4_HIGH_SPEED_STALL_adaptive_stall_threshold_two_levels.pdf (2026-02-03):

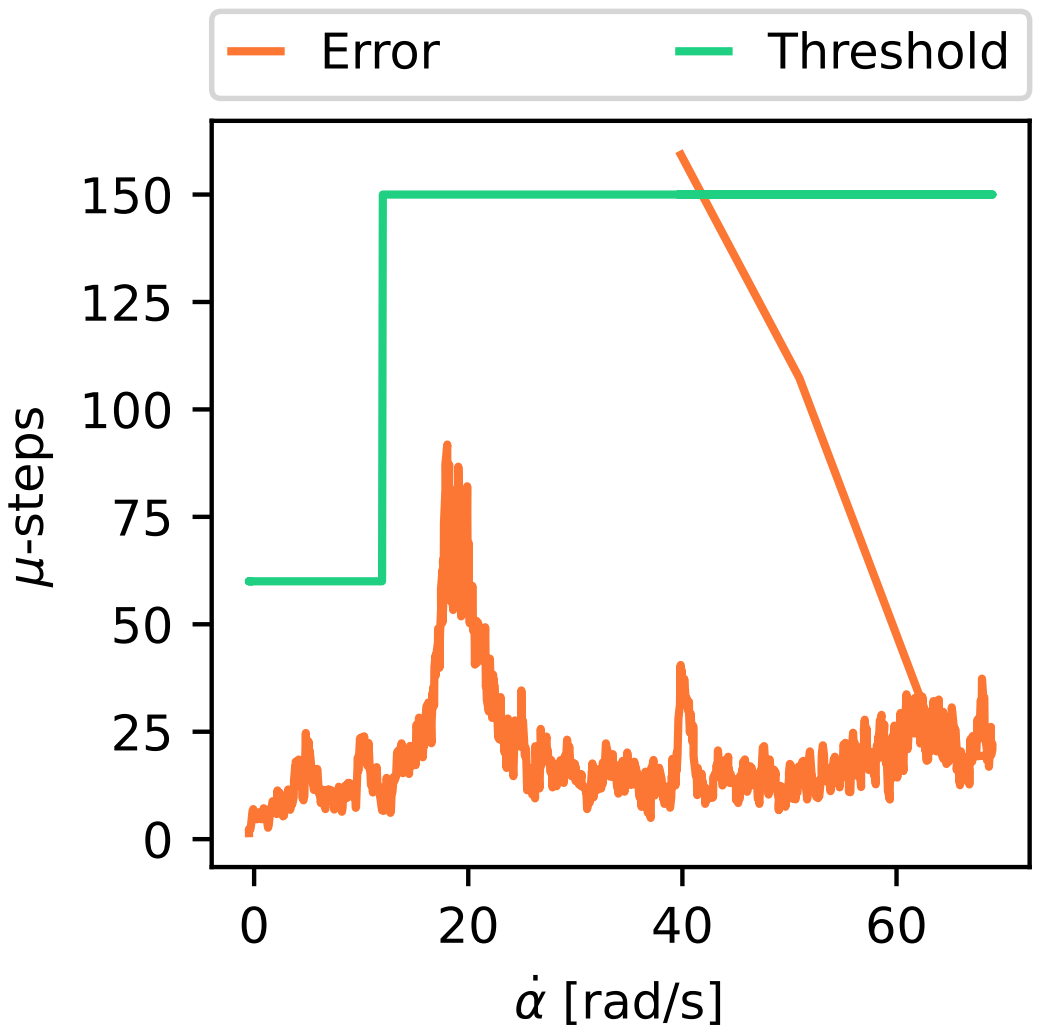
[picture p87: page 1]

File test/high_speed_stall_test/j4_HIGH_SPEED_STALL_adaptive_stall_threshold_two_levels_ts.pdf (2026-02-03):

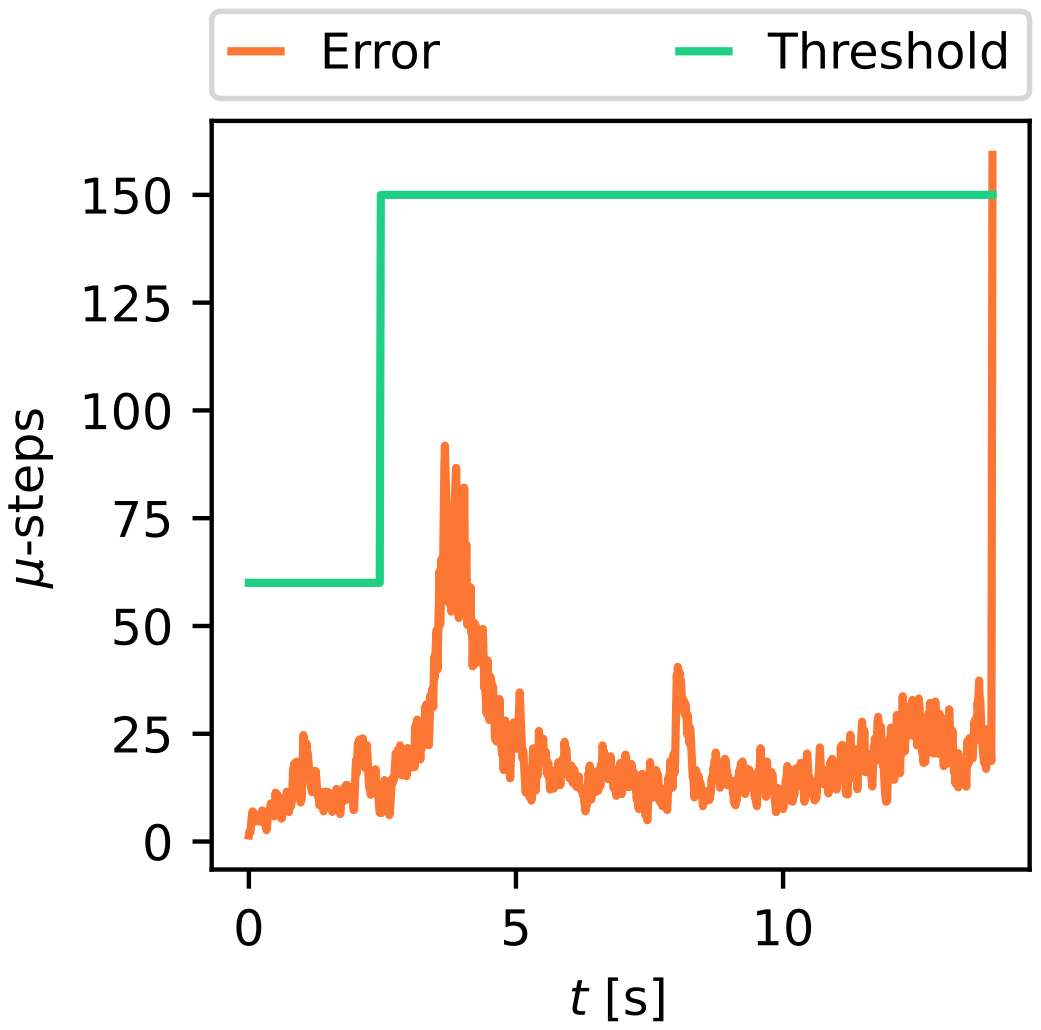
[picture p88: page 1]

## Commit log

2026-01-11 doc: joint and gripper drivers
2026-01-15 test: i2c debugging
    [sample1.CSV, sample2.CSV]
2026-01-15 add: electrical schematics
    [schematics_noGND.kicad_sch]
2026-01-16 test: add osci plots
    [100kHz.CSV, 400kHz.CSV]
2026-01-30 test: add joint vs cartesian space plots
    [cartesian_space.csv, joint_space.csv]
2026-02-02 test: i2c debugging data
    [sample1.CSV, sample2.CSV]
2026-02-03 doc: joint fw namespace
2026-02-03 test: stalldetection test
    [J3_DOWN_ramp.csv, J3_UP_ramp.csv, PID_error_test.csv, j4_HIGH_SPEED_STALL_adaptive_stall_threshold_two_levels.csv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]
2026-02-09 rename Assembly
    [80T gear.stl, Arm cover.stl, Arm link 1.stl, Arm mount.stl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]
2026-02-09 fix: hardware files
    [80T gear.stl, Arm cover.stl, Arm link 1.stl, Arm mount.stl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]
2026-02-09 add more meshes
    [80T gear.stl, Arm cover.stl, Arm link 1.stl, Arm mount.stl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]
